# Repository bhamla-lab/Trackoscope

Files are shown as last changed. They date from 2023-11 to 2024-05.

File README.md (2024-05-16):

# Trackoscope

## Programs

### TrackoscopeComm.py (MAIN PROGRAM)
This program is to be run on a laptop. It has the full organism-tracking capability and has a user-friendly GUI. Once "Start Tracking" has been clicked, the user can then select the organism that they wish to track and hit the "Enter" key on their keyboard to start the track. As the organism starts moving, the actuator moves to keep it in frame.



### Grapher.py
Taking CSV data and converting to meaningful graphs that display speed and position over the track duration.

### ArduinoMovPlat.ino
This program is to be uploaded to the Arduino Uno and enables the python code to control Trackoscope. This code also allows for pure joystick control.

### Getting Started
This project uses python virtual environments. We suggest using software such as Visual Studio Code or JetBrains Pycharm to run the code.

Open a command prompt and then install the dependencies to get it working.

    pip install -r requirements.txt

## Trackoscope Build Instructions

### Assembly
#### Document/Files
Trackoscope Assembly Instructions.PDF contains the step by step instructions on how to build a Trackoscope. All files can be found in the MakerFiles folder in the repository.

#### Additional Tools/Materials
* M5 Allen Key
* M4 Allen Key
* M3 Allen Key
* M2 Allen Key
* Flush Cutters
* Hot Glue/Super Glue

### 3D Printing
All STL files can be fit on any standard 3D printer (ender 3, prusa mini, ultimaker 3). They can be sliced with Ultimaker Cura, a free slicing software.



#### Print Settings/Layout
* 0.2 mm layer height
* 30% infill density (gyroid or tri-hexagonal pattern)
* Supports: Yes (tree)
* Adhesion: Yes (7mm  brim)

### Laser Cutting
DXF files provided are in the inches unit. They can be preppped for laser cutting using a vector modifying software such as Inkscape or Adobe Illustrator. These files are meant for 1/4" material thickness. Files that end in "TAP" have smaller hole sizes for tapping instead of clearance holes to be used with nuts and bolts. The files ending in "Spacer" are optional and can be cut if extra height is needed. There are two motor mount files. Depending on your application, the tall mount can be used.

## The Paper
Link: doi.org/10.1101/2024.02.06.579130

Supplementary Files can be found at figshare.com/account/home#/projects/200934

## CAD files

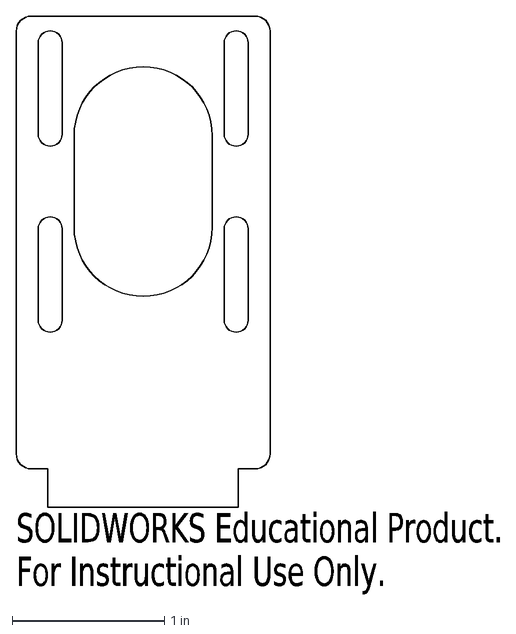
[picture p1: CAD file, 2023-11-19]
MakerFiles/AcrylicMotorMountTall.DXF
SOLIDWORKS Educational Product.
For Instructional Use Only.

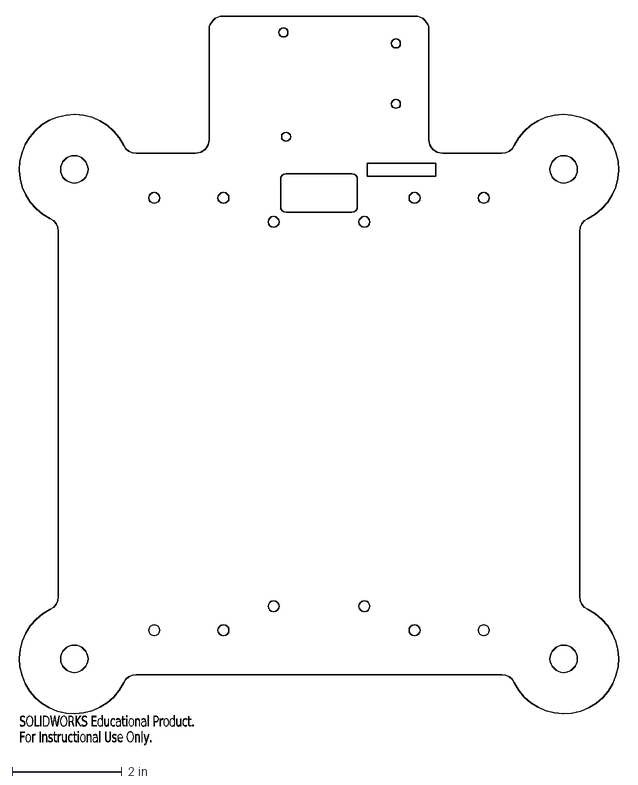
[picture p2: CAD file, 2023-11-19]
MakerFiles/AcrylicBase.DXF
SOLIDWORKS Educational Product.
For Instructional Use Only.

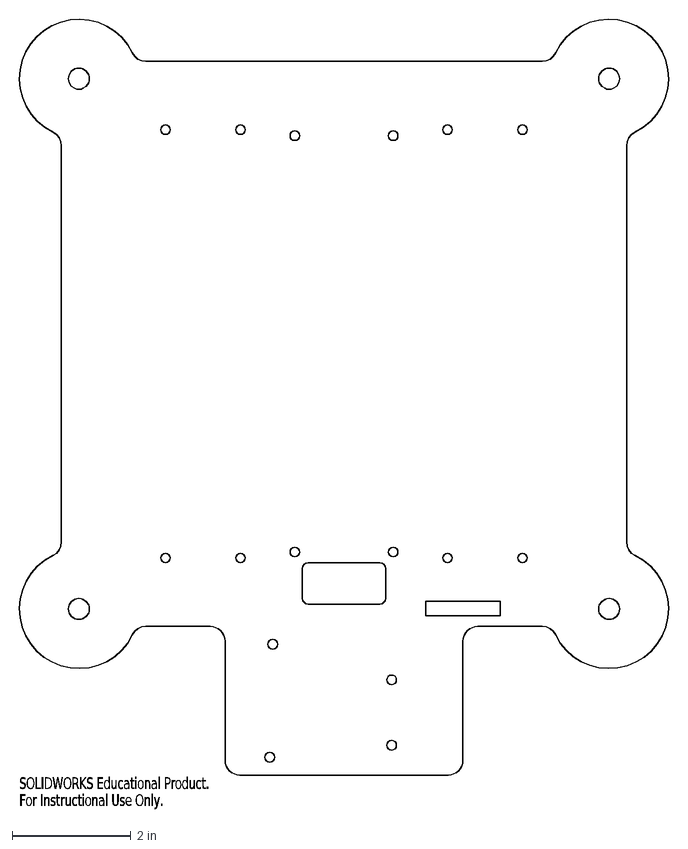
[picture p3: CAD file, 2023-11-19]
MakerFiles/AcrylicBaseTAP.DXF
SOLIDWORKS Educational Product.
For Instructional Use Only.

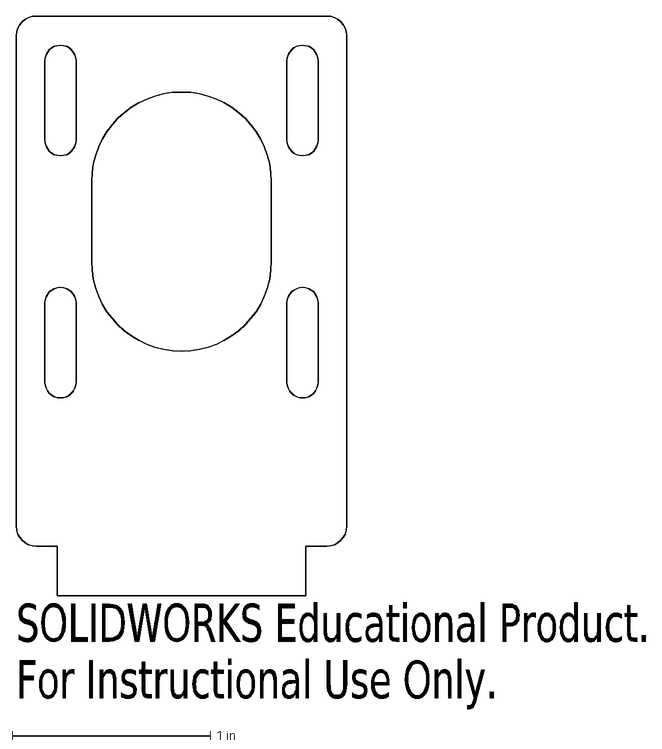
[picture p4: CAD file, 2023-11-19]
MakerFiles/AcrylicMotorMount.DXF
SOLIDWORKS Educational Product.
For Instructional Use Only.

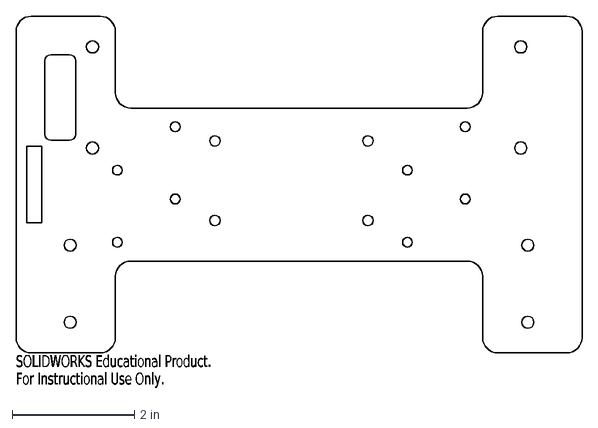
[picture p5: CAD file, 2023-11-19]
MakerFiles/AcrylicYBase.DXF
SOLIDWORKS Educational Product.
For Instructional Use Only.

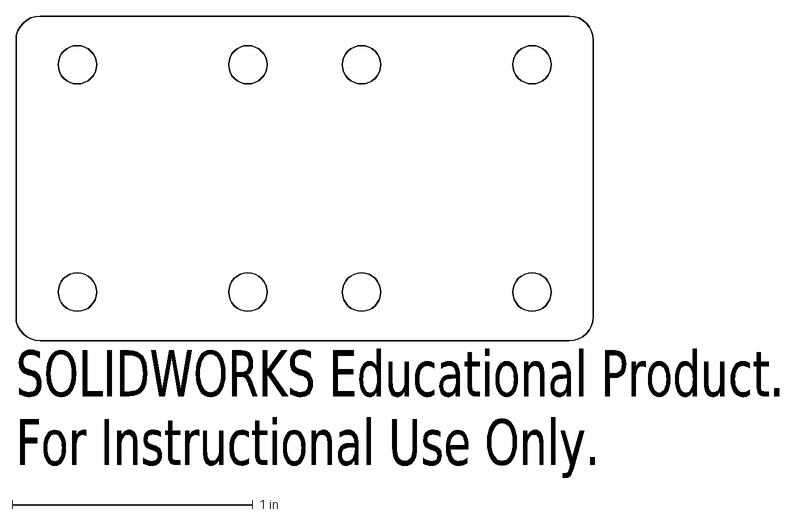
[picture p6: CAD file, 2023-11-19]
MakerFiles/LinearBearingSpacer.DXF
SOLIDWORKS Educational Product.
For Instructional Use Only.

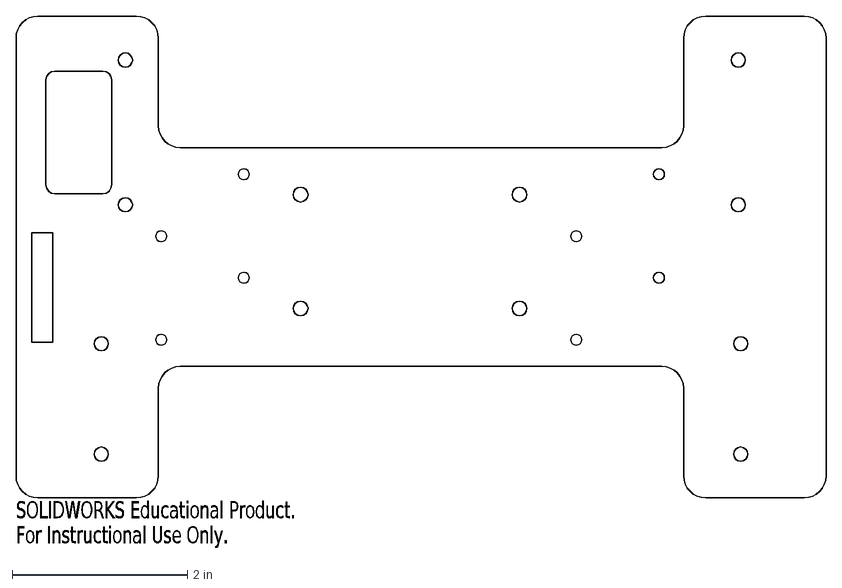
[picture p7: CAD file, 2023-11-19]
MakerFiles/AcrylicYBaseTAP.DXF
SOLIDWORKS Educational Product.
For Instructional Use Only.

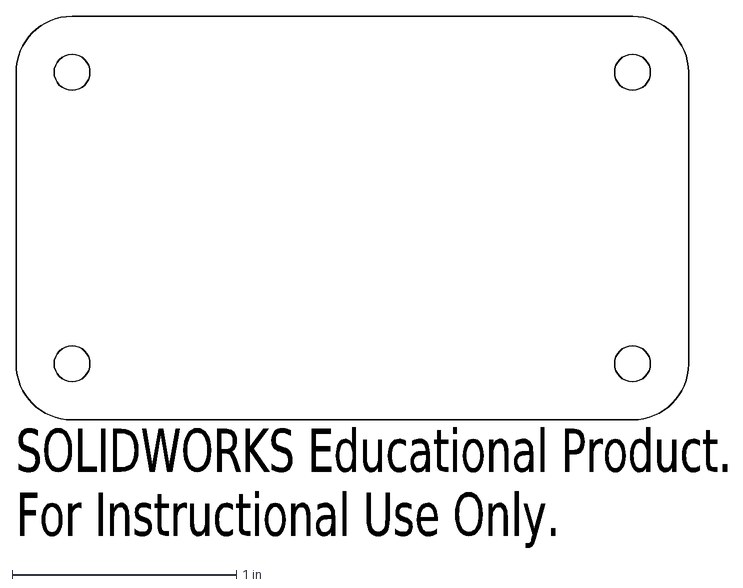
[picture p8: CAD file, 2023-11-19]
MakerFiles/XYConnectorSpacer.DXF
SOLIDWORKS Educational Product.
For Instructional Use Only.

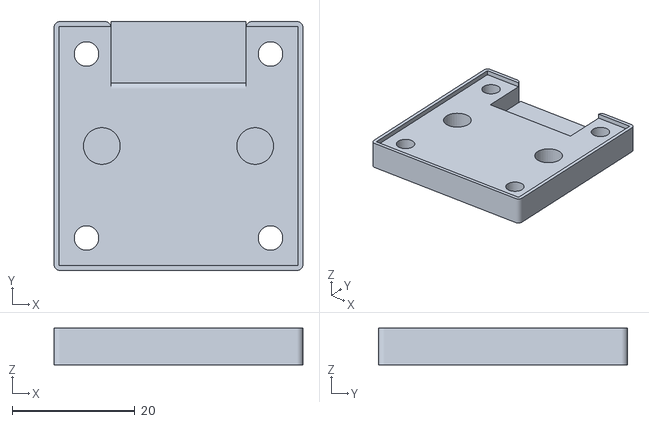
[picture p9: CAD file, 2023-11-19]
MakerFiles/HQ Pi-Cam Bot.STL
40.6 x 40.6 x 6.00

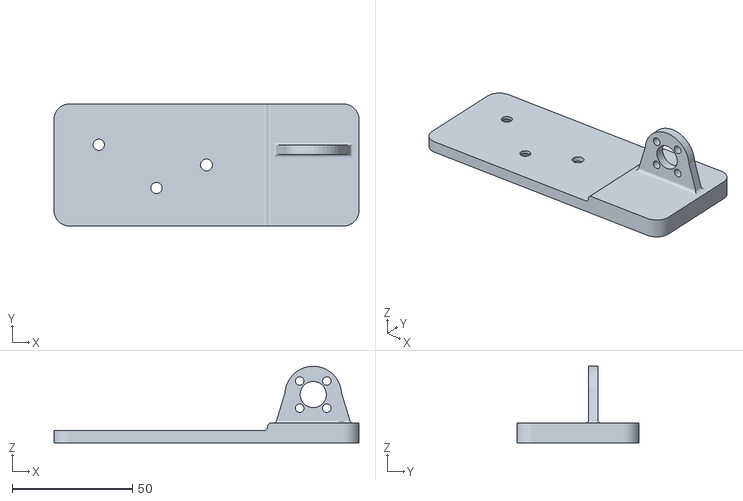
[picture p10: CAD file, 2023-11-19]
MakerFiles/OpticsHoldMag.STL
127.0 x 50.8 x 31.9

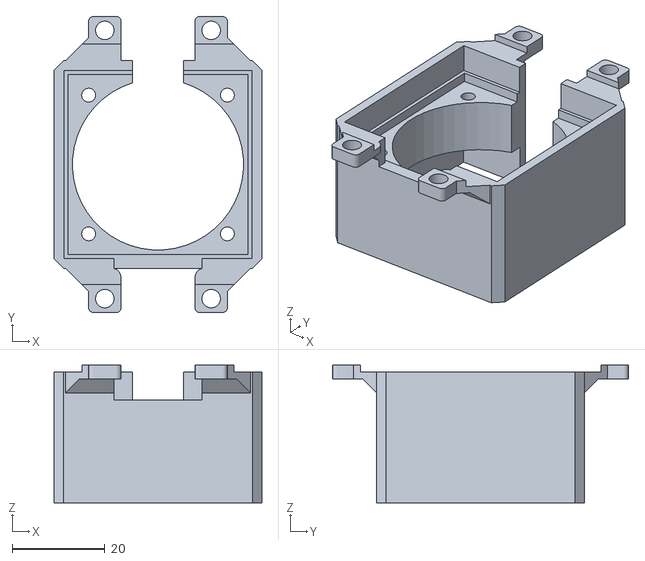
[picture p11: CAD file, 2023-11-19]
MakerFiles/HQ Pi-Cam Top.STL
44.9 x 64.0 x 29.8

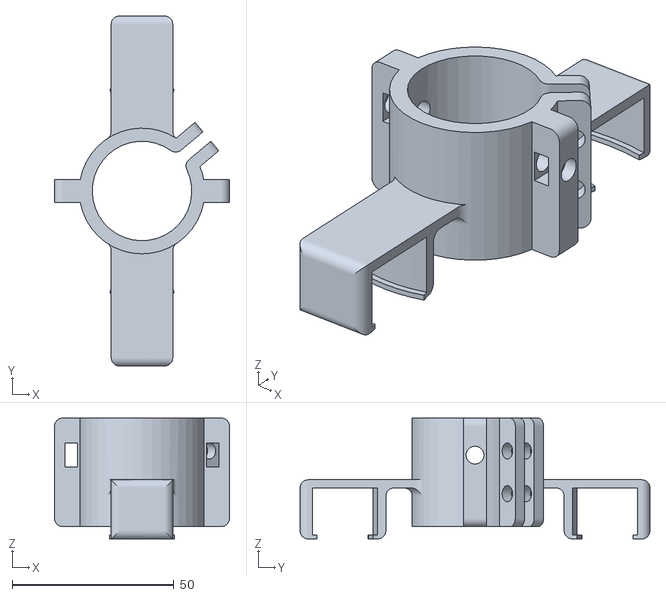
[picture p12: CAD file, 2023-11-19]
MakerFiles/CombinedHold.STL
54.1 x 108.2 x 37.3

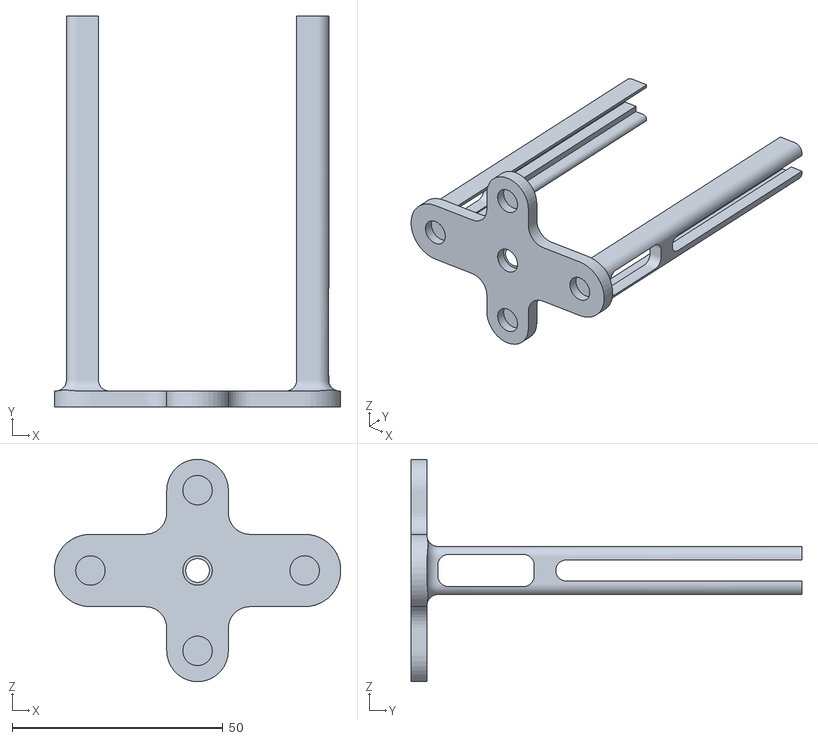
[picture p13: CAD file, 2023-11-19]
MakerFiles/MicroscopeMountMag.STL
67.9 x 92.7 x 52.7

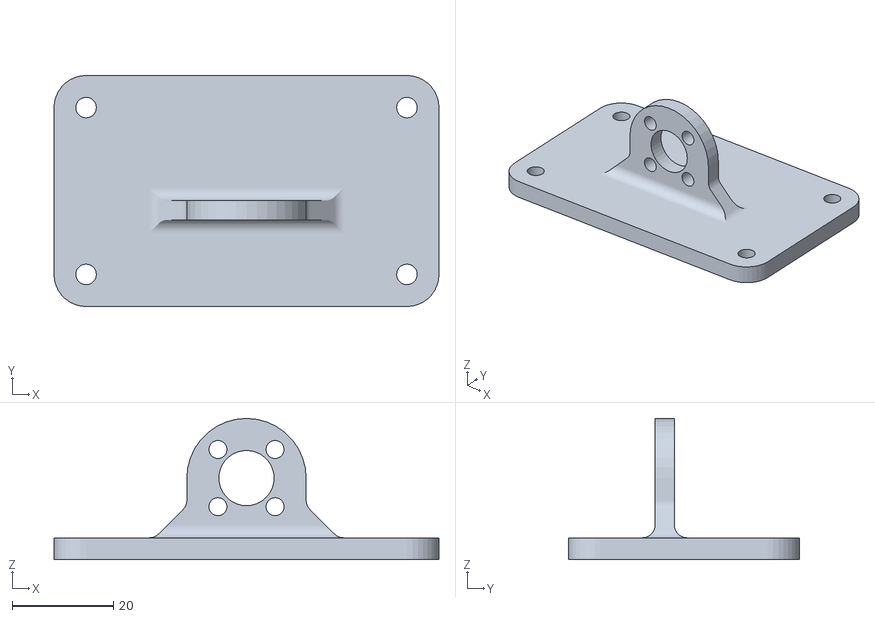
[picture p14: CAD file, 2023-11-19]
MakerFiles/XYConnector.STL
76.2 x 45.7 x 27.9

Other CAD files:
MakerFiles/KnobX2.STL

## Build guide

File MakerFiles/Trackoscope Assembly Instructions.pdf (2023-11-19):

## Trackoscope: a low-cost open tracking scope for STEM

Priya Soneji¹, Elio Challita², Saad Bhamla³

### 1 Mechanical Engineering, Georgia Institute of Technology

### 2 Biomedical Engineering, Georgia Institute of Technology

### 3 Chemical and Biomolecular Engineering, Georgia Institute of Technology

Trackoscope Assembly Instructions

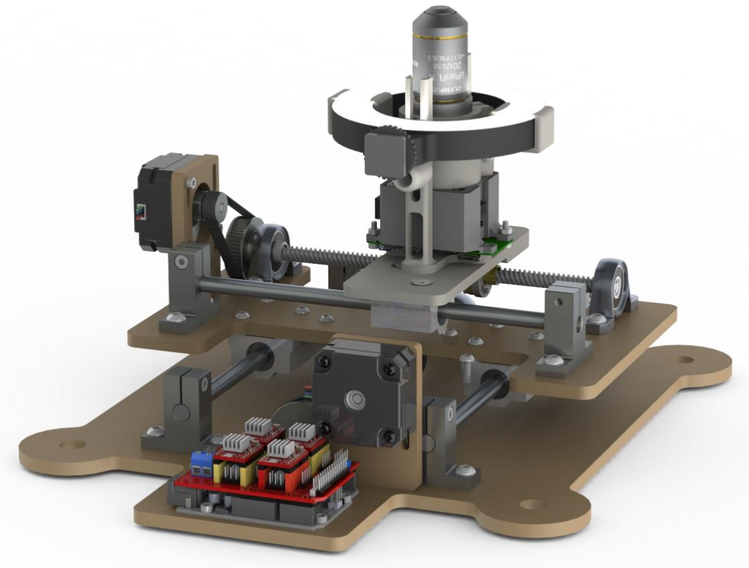
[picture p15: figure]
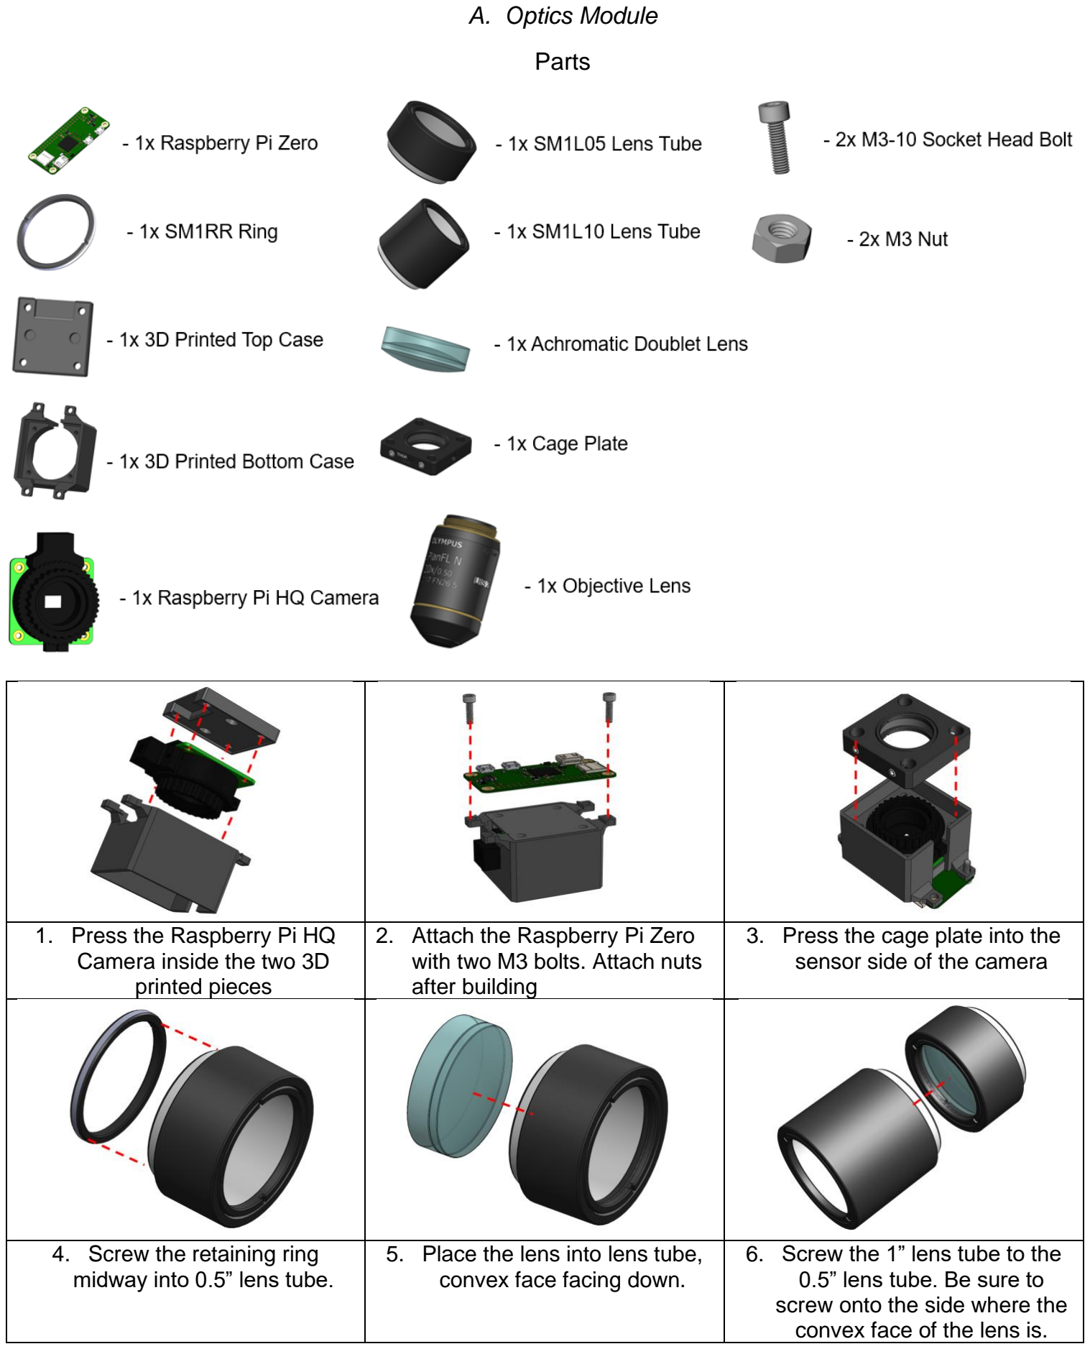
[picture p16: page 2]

A. Optics Module

Parts

1. Press the Raspberry Pi HQ Camera inside the two 3D
printed pieces
2. Attach the Raspberry Pi Zero with two M3 bolts. Attach nuts after building
3. Press the cage plate into the sensor side of the camera
4. Screw the retaining ring midway into 0.5” lens tube.
5. Place the lens into lens tube, convex face facing down.
6. Screw the 1” lens tube to the 0.5” lens tube. Be sure to screw onto the side where the convex face of the lens is.

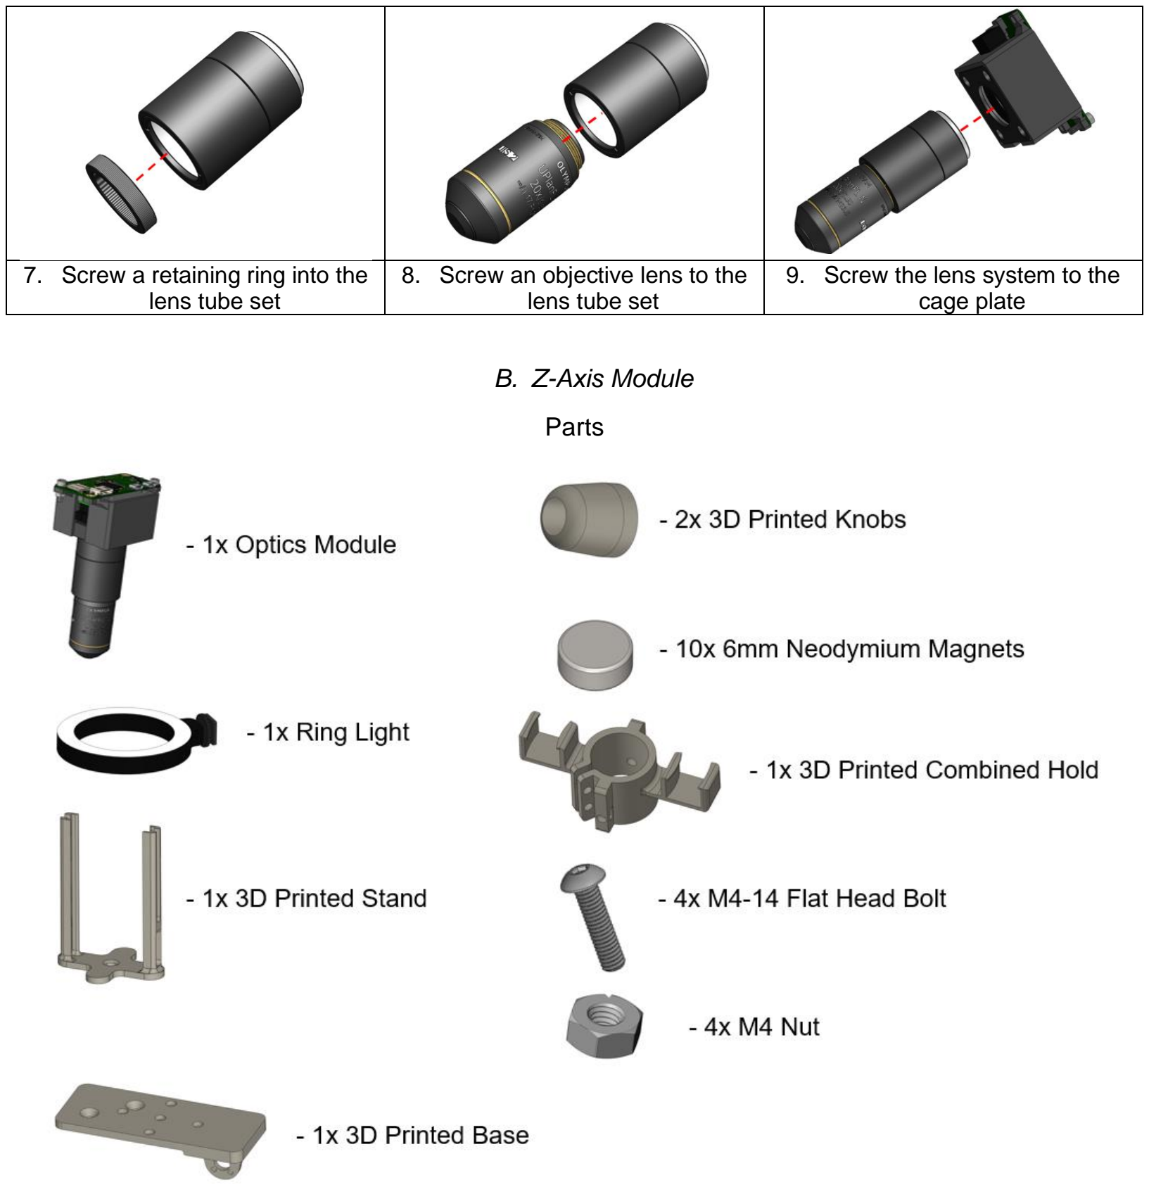
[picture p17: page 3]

7. Screw a retaining ring into the lens tube set
8. Screw an objective lens to the lens tube set
9. Screw the lens system to the cage plate
B. Z-Axis Module

Parts

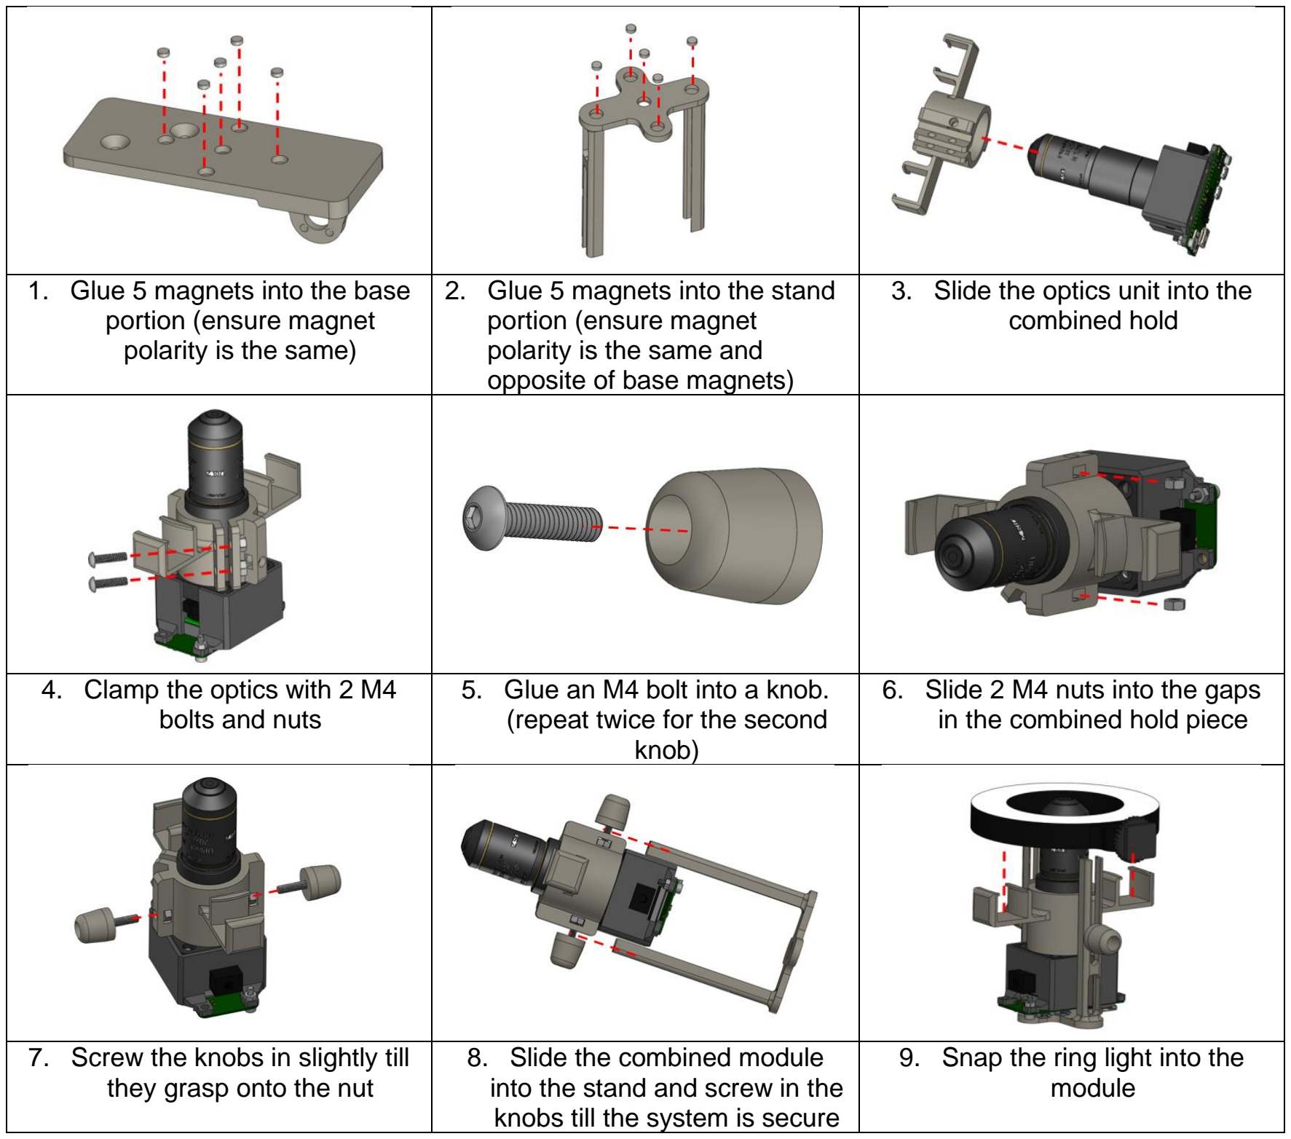
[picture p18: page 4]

1. Glue 5 magnets into the base portion (ensure magnet
polarity is the same)
2. Glue 5 magnets into the stand portion (ensure magnet
polarity is the same and
opposite of base magnets)
3. Slide the optics unit into the combined hold
4. Clamp the optics with 2 M4 bolts and nuts
5. Glue an M4 bolt into a knob. (repeat twice for the second knob)
6. Slide 2 M4 nuts into the gaps in the combined hold piece
7. Screw the knobs in slightly till they grasp onto the nut
8. Slide the combined module into the stand and screw in the knobs till the system is secure
9. Snap the ring light into the module

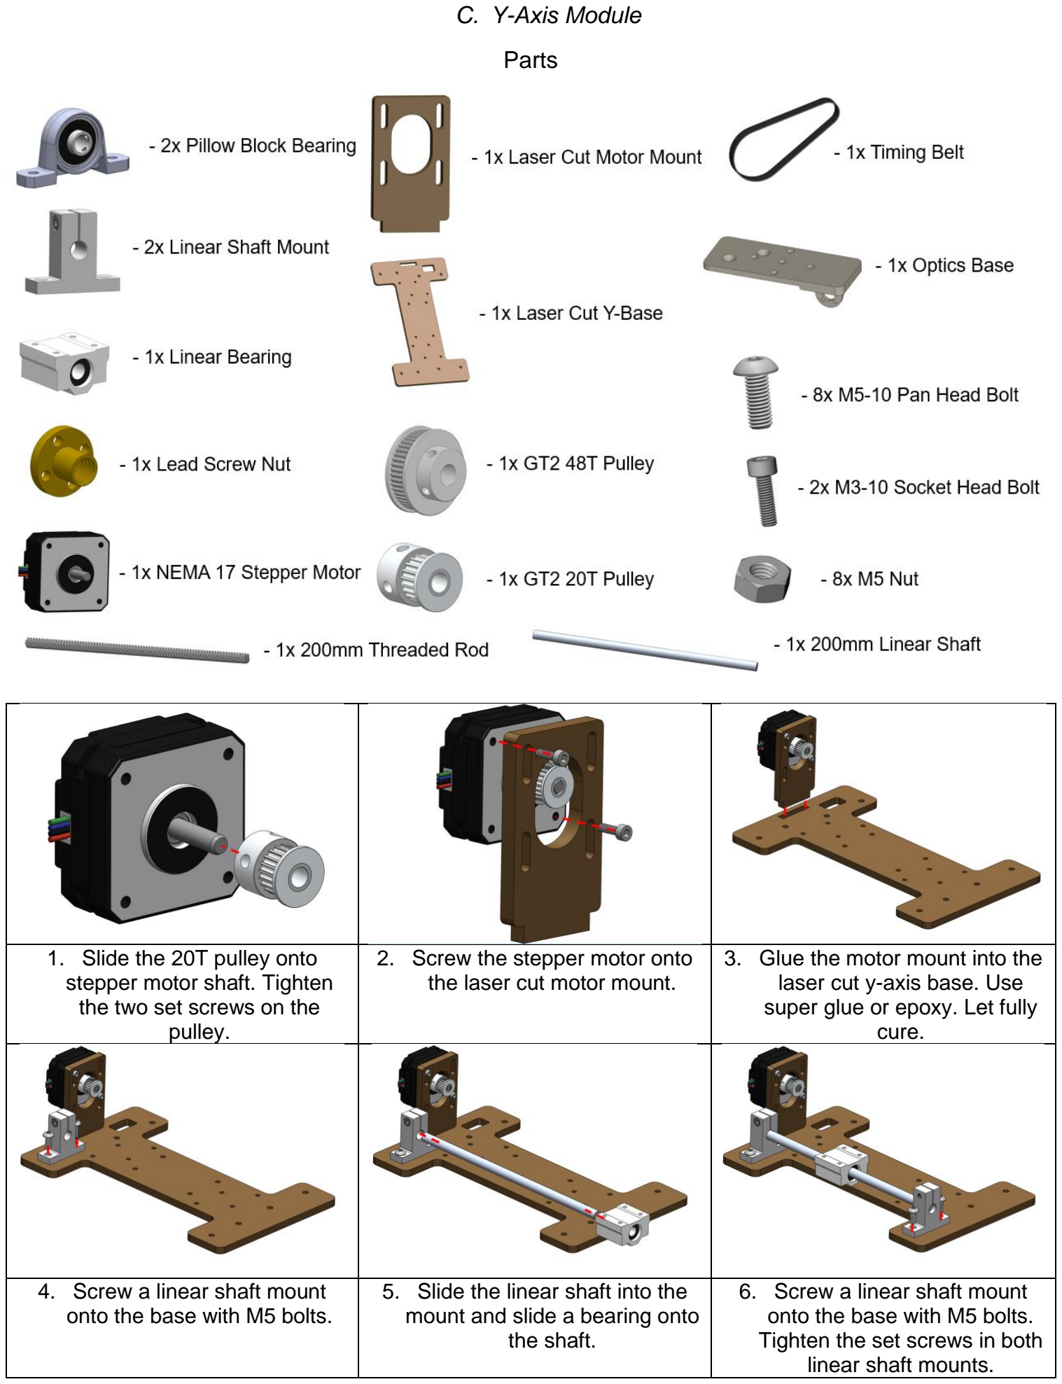
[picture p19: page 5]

C. Y-Axis Module

Parts

1. Slide the 20T pulley onto stepper motor shaft. Tighten the two set screws on the
pulley.
2. Screw the stepper motor onto the laser cut motor mount.
3. Glue the motor mount into the laser cut y-axis base. Use super glue or epoxy. Let fully cure.
4. Screw a linear shaft mount onto the base with M5 bolts.
5. Slide the linear shaft into the mount and slide a bearing onto the shaft.
6. Screw a linear shaft mount onto the base with M5 bolts. Tighten the set screws in both linear shaft mounts.

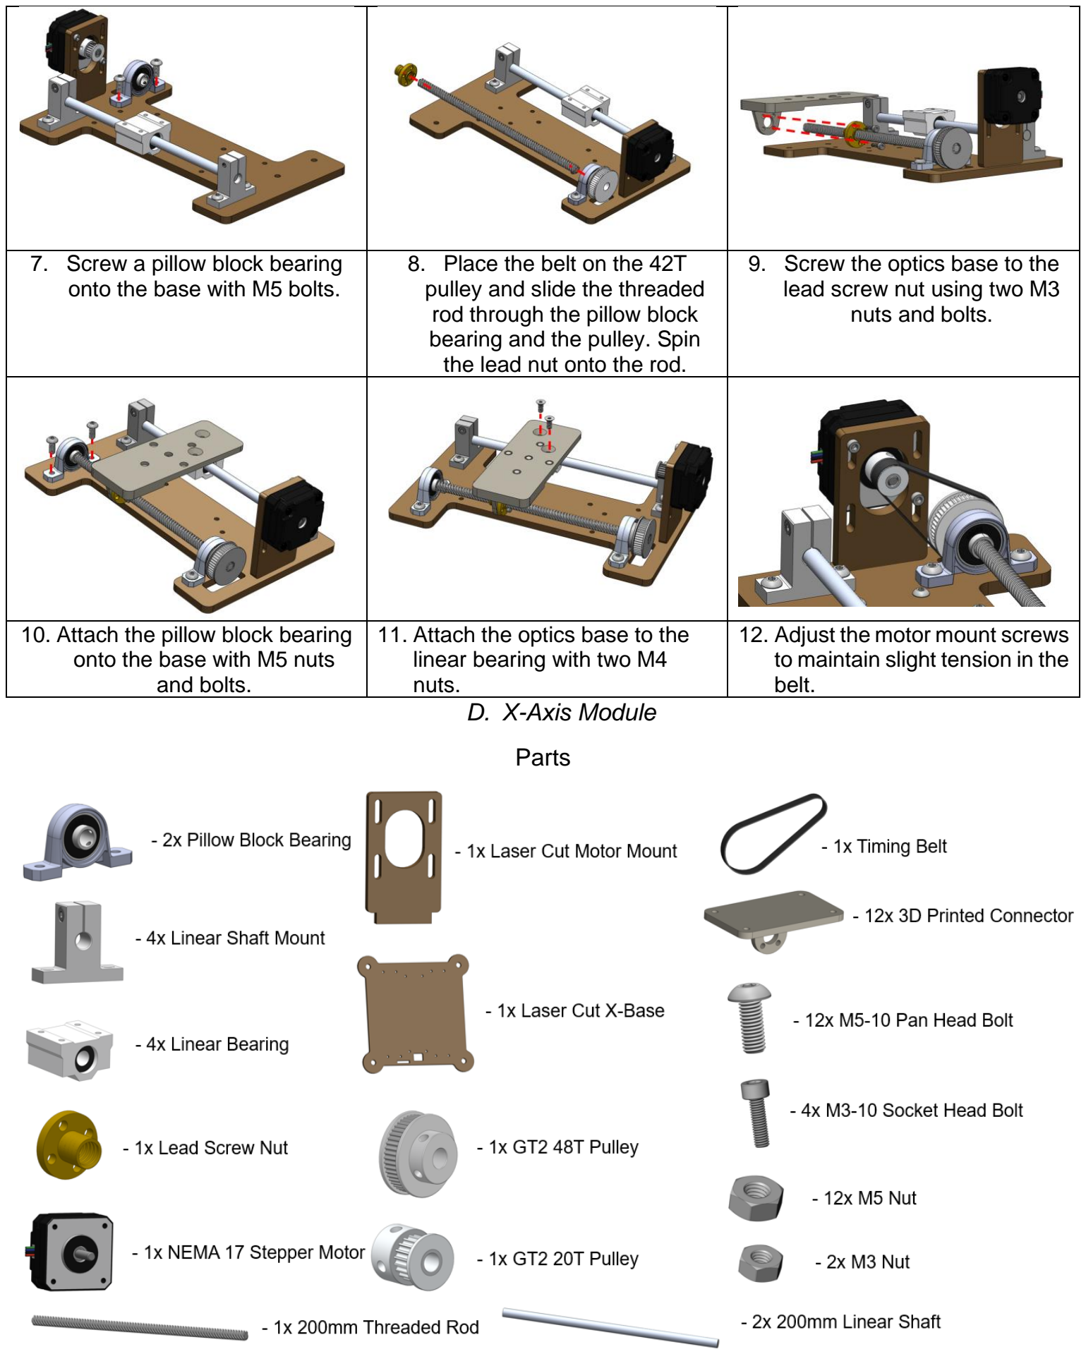
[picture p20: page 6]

7. Screw a pillow block bearing onto the base with M5 bolts.
8. Place the belt on the 42T pulley and slide the threaded rod through the pillow block bearing and the pulley. Spin the lead nut onto the rod.
9. Screw the optics base to the lead screw nut using two M3 nuts and bolts.
10. Attach the pillow block bearing onto the base with M5 nuts and bolts.
11. Attach the optics base to the linear bearing with two M4 nuts.
12. Adjust the motor mount screws to maintain slight tension in the belt.
D. X-Axis Module

Parts

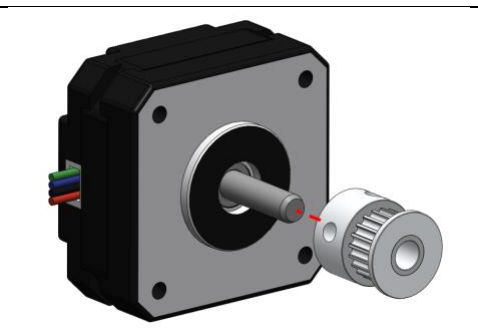
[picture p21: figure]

1. Slide the 20T pulley onto stepper motor shaft. Tighten the two set screws on the
pulley.

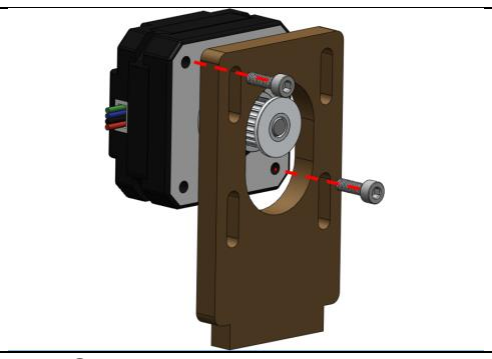
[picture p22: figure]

2. Screw the stepper motor onto the laser cut motor mount.

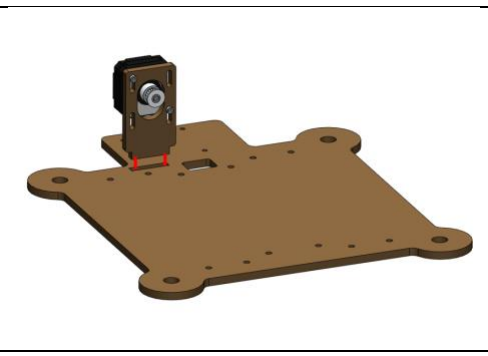
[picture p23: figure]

3. Glue the motor mount into the laser cut x-axis base. Use super glue or epoxy. Let fully cure.

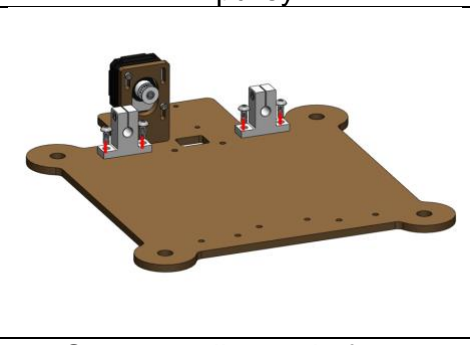
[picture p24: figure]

4. Screw two linear shaft mount onto the base with M5 bolts.

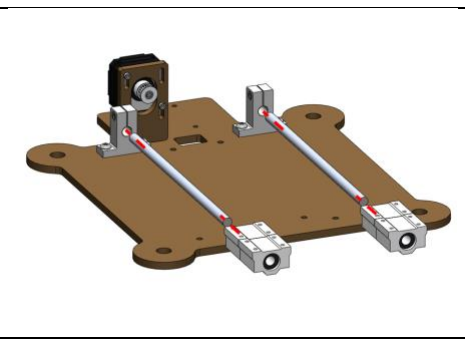
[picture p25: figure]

5. Slide the linear shafts into the mounts and slide two bearings onto each shaft.

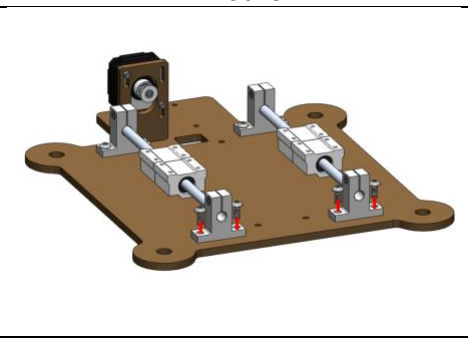
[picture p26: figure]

6. Screw two linear shaft mount onto the base with M5 bolts. Tighten the set screws in all linear shaft mounts.

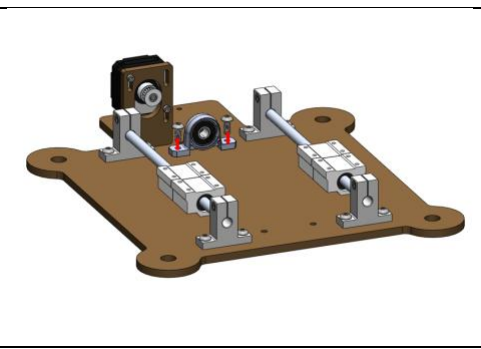
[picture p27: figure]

7. Screw a pillow block bearing onto the base with M5 bolts.

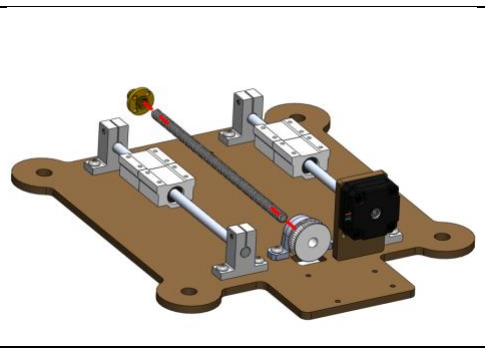
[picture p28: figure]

8. Place the belt on the 42T pulley and slide the threaded rod through the pillow block bearing and the pulley. Spin the lead screw nut onto the rod.

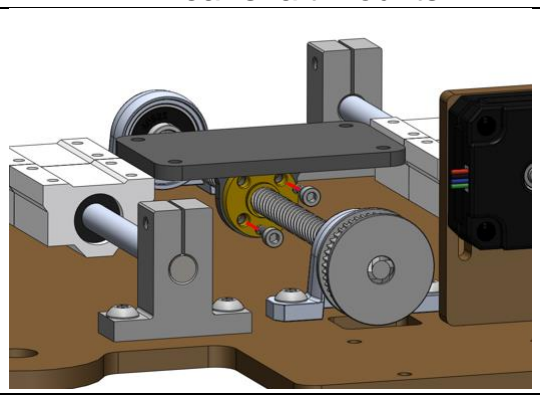
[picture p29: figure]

9. Slide the XY connector onto the threaded rod and secure onto the lead screw nut with 2 M3 bolts and 2 M3 nuts.

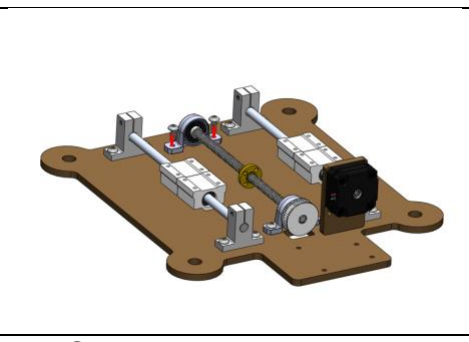
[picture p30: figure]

10. Screw a pillow block bearing onto the base with M5 bolts. Tighten the set screws on the pillow block bearings.

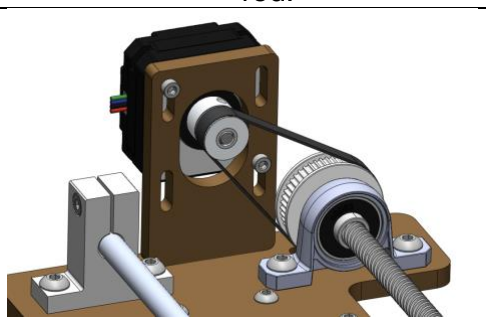
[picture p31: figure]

11. Adjust the motor mount screws to maintain slight tension in the belt.

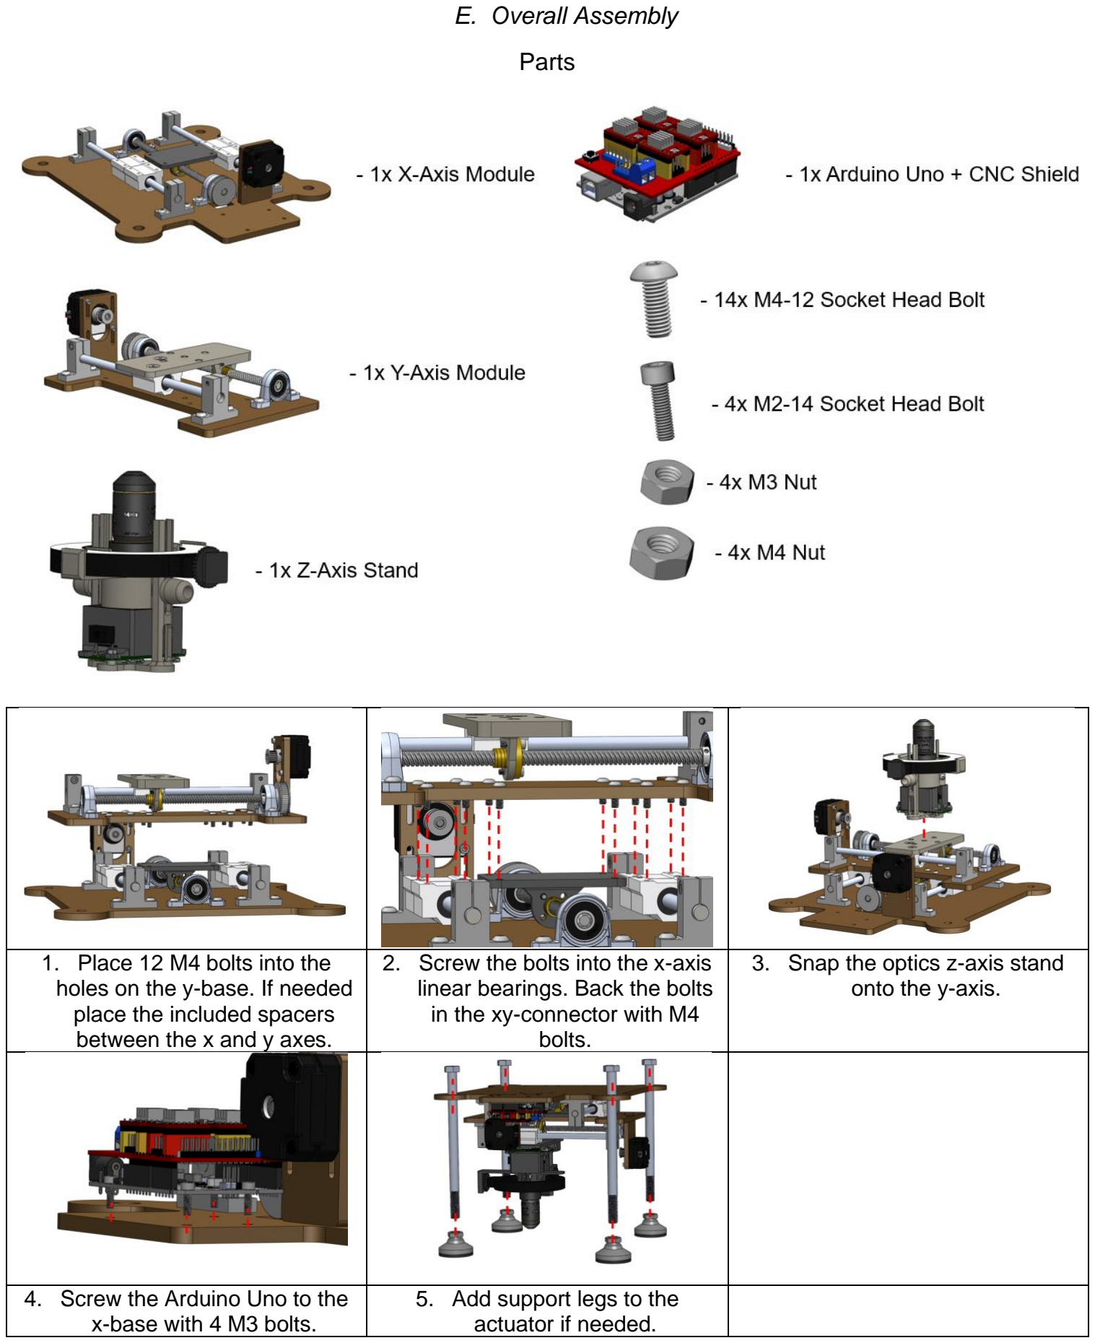
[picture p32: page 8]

E. Overall Assembly

Parts

1. Place 12 M4 bolts into the holes on the y-base. If needed place the included spacers between the x and y axes.
2. Screw the bolts into the x-axis linear bearings. Back the bolts in the xy-connector with M4 bolts.
3. Snap the optics z-axis stand onto the y-axis.
4. Screw the Arduino Uno to the x-base with 4 M3 bolts.
5. Add support legs to the actuator if needed.

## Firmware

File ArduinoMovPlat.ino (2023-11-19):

#define EN        8      //Stepper Motor Enable, Active Low Level 
#define X_DIR    5      //X-Axis Stepper Motor Direction Control 
#define Y_DIR    6     //Y-Axis Stepper Motor Direction Control 
#define X_STP    2    //X-Axis Stepper Control 
#define Y_STP   3    //Y-Axis Stepper Control

#define VRX_PIN  A1 // Arduino pin connected to VRX pin
#define VRY_PIN  A0 // Arduino pin connected to VRY pin
#define SW_PIN   13  // Arduino pin connected to SW  pin

int dirx =0;
int stepss = 50;
int stepsl = 10;
char chardir;
int diry = 0;

int xValue = 0; // To store value of the X axis
int yValue = 0; // To store value of the Y axis
int bValue = 0; // To store value of the button

uint8_t btn_prev;
boolean joymove = false;

void step(boolean dir, byte dirPin, byte stepperPin, int steps)
{
  digitalWrite(dirPin, dir);
  for (int i = 0; i < steps; i++) {
    digitalWrite(stepperPin, HIGH);
    delayMicroseconds(800);
    digitalWrite(stepperPin, LOW);
    delayMicroseconds(800);
  }
  delayMicroseconds(100);
}


void setup() {
  pinMode(X_DIR, OUTPUT);
  pinMode(X_STP, OUTPUT);
  pinMode(Y_DIR, OUTPUT); 
  pinMode(Y_STP, OUTPUT);
  pinMode(SW_PIN, INPUT_PULLUP);
  btn_prev = digitalRead(SW_PIN);
  pinMode(EN, OUTPUT);
  digitalWrite(EN, HIGH);
  Serial.begin(2000000);
}

void loop() {
  uint8_t btn = digitalRead(SW_PIN);
  if (btn == LOW && btn_prev == HIGH){
    joymove = !joymove;
    Serial.print("button pressed");
    delayMicroseconds(1500);
  }
  btn_prev = digitalRead(SW_PIN);

  if(joymove) {
    xValue = analogRead(VRX_PIN);
    yValue = analogRead(VRY_PIN);

    if (yValue > 750) {
      digitalWrite(EN, LOW);
      diry = 1;
      Serial.print("going up");
    } else if (yValue < 250) {
      digitalWrite(EN, LOW);
      diry = -1;
      Serial.print("going down");
    } else {
      diry = 0;
    }

    if (xValue > 750) {
      digitalWrite(EN, LOW);
      dirx = 1;
      Serial.print("going right");
    } else if (xValue < 250) {
      digitalWrite(EN, LOW);
      dirx = -1;
      Serial.print("going left");
    } else {
      dirx = 0;
    }

    if (dirx == 0 and diry == 0) {
      digitalWrite(EN, HIGH);
    }
    
  }
  
  if (Serial.available() and !joymove) {
//    chardir = (Serial.readString()).charAt(0);
    chardir = Serial.read();
    // Code for Camera Mode
    if (chardir == 'L') {
      digitalWrite(EN, LOW);
      dirx = -1;
      chardir = 'N';
    }
    else if (chardir == 'R') {
      digitalWrite(EN, LOW);
      dirx = 1;
      chardir = 'N';
    }
    else if (chardir == 'U') {
      digitalWrite(EN, LOW);
      diry = -1;
      chardir = 'N';
    }
    else if (chardir == 'D') {
      digitalWrite(EN, LOW);
      diry = 1;
      chardir = 'N';
    }
    else if (chardir == 'X') {
      digitalWrite(EN, LOW);
      dirx = 0;
      chardir = 'N';
    }
    else if (chardir == 'Y') {
      digitalWrite(EN, LOW);
      diry = 0;
      chardir = 'N';
    }

    // Stop all if nothing
    if ((((dirx == 0) && (diry == 0)) || (chardir == 'S')|| (chardir == 's'))) {
      digitalWrite(EN, LOW);
      dirx = 0;
      diry = 0;
      chardir = 'N';
    }
    
    // Stop hard stop
    if (chardir == 'E') {
      digitalWrite(EN, HIGH);
      dirx = 0;
      diry = 0;
      chardir = 'N';
    }
  }

  // Moving the platform
  if (dirx == -1) {
    step(false, X_DIR, X_STP, stepsl);
  }
  if (dirx == 1) {
    step(true, X_DIR, X_STP, stepsl);
  }
  if (diry == -1) {
    step(false, Y_DIR, Y_STP, stepsl);
  }
  if (diry == 1) {
    step(true, Y_DIR, Y_STP, stepsl);
  }
}

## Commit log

2023-11-19 3d prints
    [CombinedHold.STL, HQ Pi-Cam Bot.STL, HQ Pi-Cam Top.STL, KnobX2.STL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]
2023-11-19 Laser Files
    [AcrylicBase.DXF, AcrylicBaseTAP.DXF, AcrylicMotorMount.DXF, AcrylicMotorMountTall.DXF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]
2023-11-19 Assembly Instructions
2023-11-19 Update and rename XYConnector.DXF to XYConnectorSpacer.DXF
    [XYConnectorSpacer.DXF]
2023-11-19 Update and rename PrintSettings.md to MakingSettings.md
